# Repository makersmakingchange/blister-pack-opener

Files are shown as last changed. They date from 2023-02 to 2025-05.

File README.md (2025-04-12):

# Blister Pack Opener
The Blister Pack Opener is designed to help users with arthritis or limited hand strength open blister packs of pills.

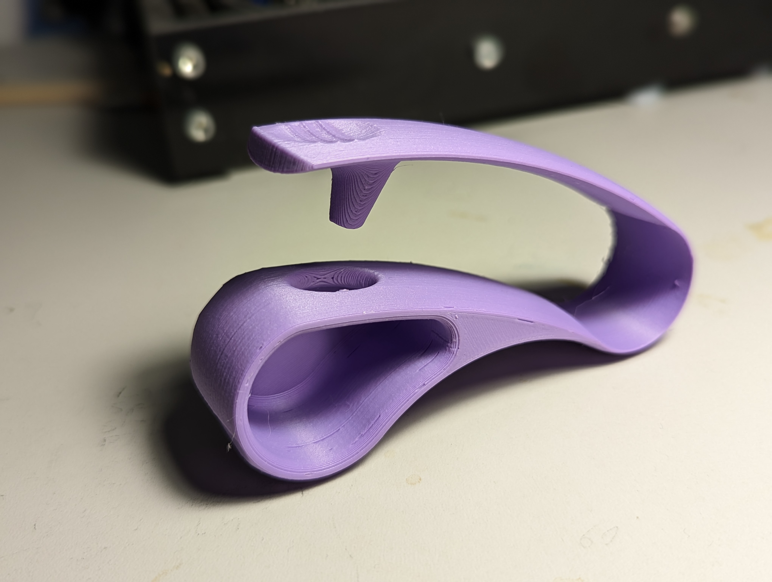
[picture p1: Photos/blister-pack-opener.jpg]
Picture of Blister Pack Opener.


## More info at
- [Makers Making Change Project Page](https://www.makersmakingchange.com/s/product/blister-pack-opener/01tJR0000009H85YAE)

## How to Obtain a Blister Pack Opener
### 1. Do it Yourself (DIY) or Do it Together (DIT)

This is an open-source assistive technology, so anyone is free to build it. All of the files and instructions required to build the Blister Pack Opener are contained within this repository. Refer to the Maker Checklist below.

### 2. Request a build of this device

If you would like to obtain a Blister Pack Opener, you may submit a build request through the [MMC Library Page](https://www.makersmakingchange.com/s/product/blister-pack-opener/01tJR0000009H85YAE). The requestor is responsible for the cost of materials and any shipping.

### 3. How to build this device for someone else

If you have the skills and equipment to build this device, and would like to donate your time to create the switch for someone who needs it, visit the [MMC Maker Wanted](https://makersmakingchange.com/maker-wanted/) section.

## Getting Started

### 1. Read the Makers Checklist

[The Makers Checklist](/Documentation/Blister_Pack_Opener_Maker_Checklist_V1.0.pdf)

### 2. Order the Off-The-Shelf Components

The [Bill of Materials](/Documentation/Blister_Pack_Opener_BOM_V1.0.xlsx) lists all of the parts and components required to build the Blister Pack Opener. 

### 3. Print the 3D Printable components

All of the files and individual print files can be in the [/Build_Files/3D_Printing_Files](/Build_Files/3D_Printing_Files/) folder.

## Files
### Documentation
| Document             | Version | Link |
|----------------------|---------|------|
| Design Rationale     | 1.0     | [Blister_Pack_Opener_Design_Rationale](/Documentation/Blister_Pack_Opener_Design_Rationale_V1.0.pdf)     |
| Maker Checklist      | 1.0     | [Blister_Pack_Opener_Maker_Checklist](/Documentation/Blister_Pack_Opener_Maker_Checklist_V1.0.pdf)     |
| Bill of Materials    | 1.0     | [Blister_Pack_Opener_Bill_of_Materials](/Documentation/Blister_Pack_Opener_BOM_V1.0.xlsx)     |
| 3D Printing Guide    | 1.0     | [Blister_Pack_Opener_3D_Printing_Guide](/Documentation/Blister_Pack_Opener_3D_Printing_Guide_V1.0.pdf)     |
| Assembly Guide       | 1.0     | [Blister_Pack_Opener_Assembly_Guide](/Documentation/Blister_Pack_Opener_Assembly_Guide_V1.0.pdf)     |
| User Guide           | 1.0     | [Blister_Pack_Opener_User_Guide](/Documentation/Blister_Pack_Opener_User_Guide_V1.0.pdf)    |
| Changelog            | 1.0     | [Blister_Pack_Opener_Changelog](/Documentation/Blister_Pack_Opener_Changelog_V1.0.pdf)     |

### Design Files
 - [CAD Files](/Design_Files/CAD_Files)

### Build Files
 - [3D Printing Files](/Build_Files/3D_Printing_Files)

## Attribution

Designers:
 - Design and documentation by Neil Squire Society/Makers Making Change

## License
Everything needed or used to design, make, test, or prepare the Blister Pack Opener is licensed under the [Attribution-NonCommercial-ShareAlike 4.0 ](https://creativecommons.org/licenses/by-nc-sa/4.0/).

Accompanying material such as instruction manuals, videos, and other copyrightable works that are useful but not necessary to design, make, test, or prepare the Blister Pack Opener are published under a Creative Commons Attribution-ShareAlike 4.0 license https://creativecommons.org/licenses/by-sa/4.0/ (CC BY-SA 4.0).

---

<!-- ABOUT MMC START -->
## About Makers Making Change
[Makers Making Change Logo](https://www.makersmakingchange.com/)

Makers Making Change is a program of [Neil Squire](https://www.neilsquire.ca/), a Canadian non-profit that uses technology, knowledge, and passion to empower people with disabilities.

Makers Making Change leverages the capacity of community based Makers, Disability Professionals and Volunteers to develop and deliver affordable Open Source Assistive Technologies.

 - Website: [www.MakersMakingChange.com](https://www.makersmakingchange.com/)
 - GitHub: [makersmakingchange](https://github.com/makersmakingchange)
 - Bluesky: [@makersmakingchange.bsky.social](https://bsky.app/profile/makersmakingchange.bsky.social)
 - Instagram: [@makersmakingchange](https://www.instagram.com/makersmakingchange)
 - Facebook: [makersmakechange](https://www.facebook.com/makersmakechange)
 - LinkedIn: [Neil Squire Society](https://www.linkedin.com/company/neil-squire-society/)
 - Thingiverse: [makersmakingchange](https://www.thingiverse.com/makersmakingchange/about)
 - Printables: [MakersMakingChange](https://www.printables.com/@MakersMakingChange)

### Contact Us
For technical questions, to get involved, or to share your experience we encourage you to [visit our website](https://www.makersmakingchange.com/) or [contact us](https://www.makersmakingchange.com/s/contact).
<!-- ABOUT MMC END -->

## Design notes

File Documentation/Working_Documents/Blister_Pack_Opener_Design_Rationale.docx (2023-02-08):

# Introduction

The Blister Pack Opener is designed to help users with arthritis or limited hand strength open blister packs of pills.

# Research

Name | Picture | Price | Link

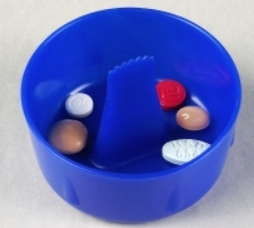
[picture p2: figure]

Blister Pack Opener | | Not Available | Link (https://at-aust.org/items/6725)

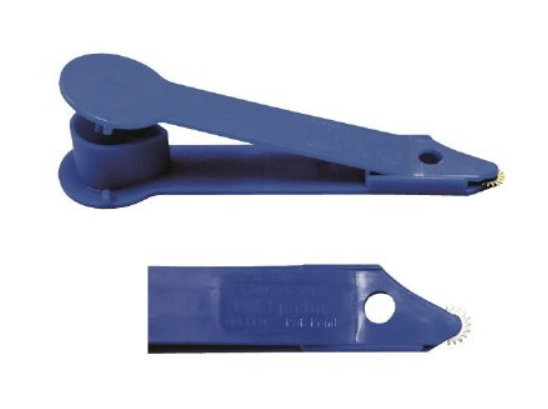
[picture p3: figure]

Pill Ejector | | $7.79 | Link (https://www.ocelco.com/store/pc/Pill-Ejectors-c1835.htm)

# Requirements

## Goals

G01 | The device must open blister packs with minimal force

## Functional Requirements

F01 | The device must be operated with one hand
F02 | The device should allow for opening blister packs using the whole hand
F03 | The device should allow for opening blister packs with minimal force

## Non-functional Requirement

NF01 | The device must be printable with no supports

## Constraints

C01 | Must be entirely 3D printed

# Testing

The device was tested on various blister packs, it worked well on smaller pills, but was too small to accommodate Day-Quil blister packs.

# Opportunities for Improvement

The hole could be made larger to accommodate for larger pills.

© 2023 by Neil Squire. This work is licensed under the CC BY SA 4.0 License: http://creativecommons.org/licenses/by-sa/4.0 Files available at https://makersmakingchange.com/project/blister-pack-opener/ Page 1 of 1

V1.0 | February 2023 Blister Pack Opener Design Rationale

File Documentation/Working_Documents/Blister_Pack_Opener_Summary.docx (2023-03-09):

# Title

Blister Pack Opener

## Subtitle

The Blister Pack Opener is designed to help users with arthritis or limited hand strength open blister packs of pills.

## Device Details

### Overview

The Blister Pack Opener is designed to help users with arthritis or limited hand strength open blister packs of pills.

### Usage

To use, place the blister pack so the flat side is over the hole, and the pill is facing the pin. Squeeze the handle so that the pill is popped out of the blister pack so that the pill pops out into the pocket in the handle.

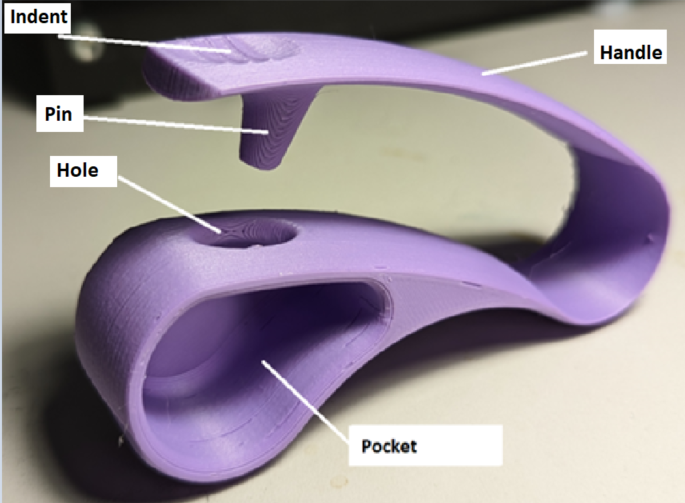
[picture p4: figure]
Blister Pack opener with all features labeled

### Cost

<$1

#### Skills Required

- 3D Printing

#### Time Required

- 3D printing time: 2h58min

#### Tools

- 3D Printer

### Attribution

- Design and documentation by Neil Squire Society/Makers Making Change

© 2023 by Neil Squire. This work is licensed under the CC BY SA 4.0 License: http://creativecommons.org/licenses/by-sa/4.0 Files available at https://makersmakingchange.com/project/blister-pack-opener/ Page 1 of 1

V1.0 | February 2023 Blister Pack Opener Summary

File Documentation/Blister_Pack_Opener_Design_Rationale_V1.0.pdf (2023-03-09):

V1.0 | February 2023

## Blister Pack Opener

## DESIGN RATIONALE

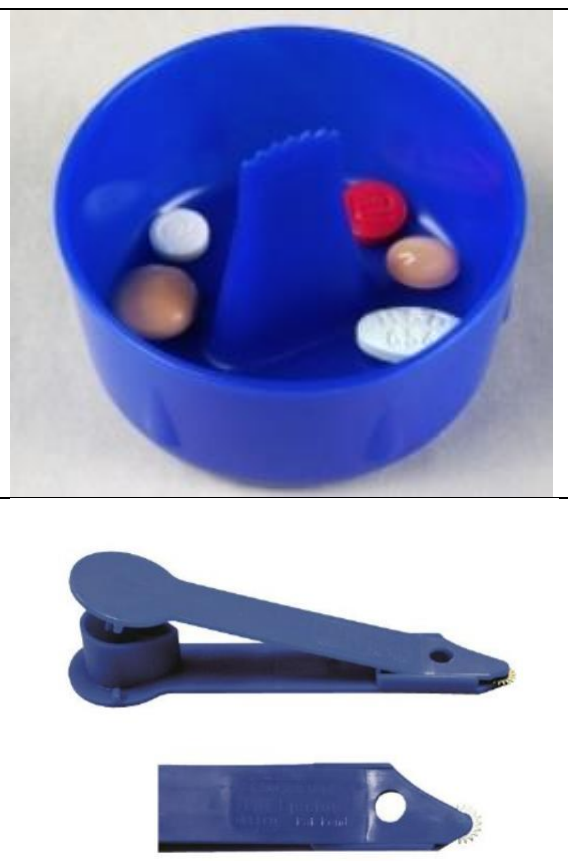
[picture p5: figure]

© 2023 by Neil Squire. (https://neilsquire.ca/)
This work is licensed under the CC BY SA 4.0 License: http://creativecommons.org/licenses/by-sa/4.0
Files available at https://makersmakingchange.com/project/blister-pack-opener/ | Page 1 of 15

### Introduction

The Blister Pack Opener is intended to make it easier to remove medication (e.g., pills) from blister packs. This may be useful for people with limited hand strength or dexterity, such as those with arthritis.

### Research

### Commercial Options

Existing commercial solutions were found by doing a web search for ‘Pill Opener’ and ‘Blister Pack Opener’.

Name | Picture | Price | Link
Blister Pack Opener | | Not Available | Link (https://at-aust.org/items/6725)
Pill Ejector | | $7.79 | Link (https://www.ocelco.com/store/pc/Pill-Ejectors-c1835.htm)

## DESIGN RATIONALE

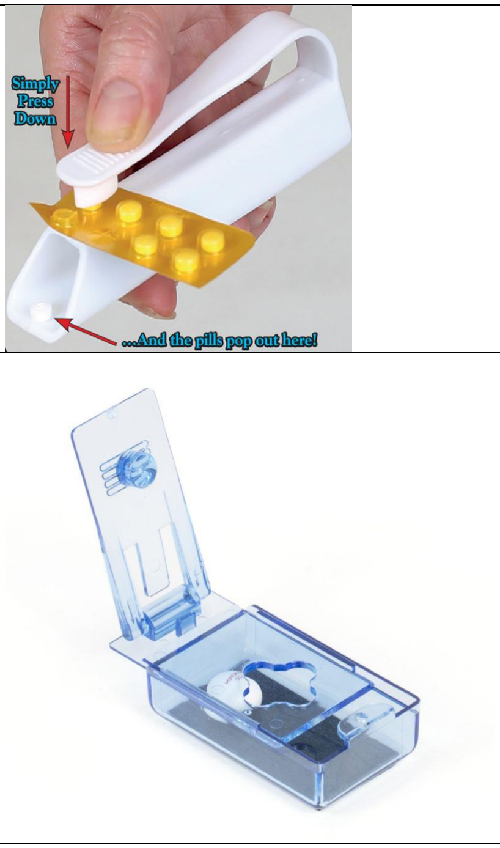
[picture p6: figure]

Files available at https://makersmakingchange.com/project/blister-pack-opener/ | Page 2 of 15

Easy
Open
Pill
Popper
Tool
$8.90 | Link (https://www.healthpride.com.au/product/Easy-Open-Pill-Popper-Tool/1876)

Tablet
Puncher
– Blister
Opener
n/a | n/a

## DESIGN RATIONALE

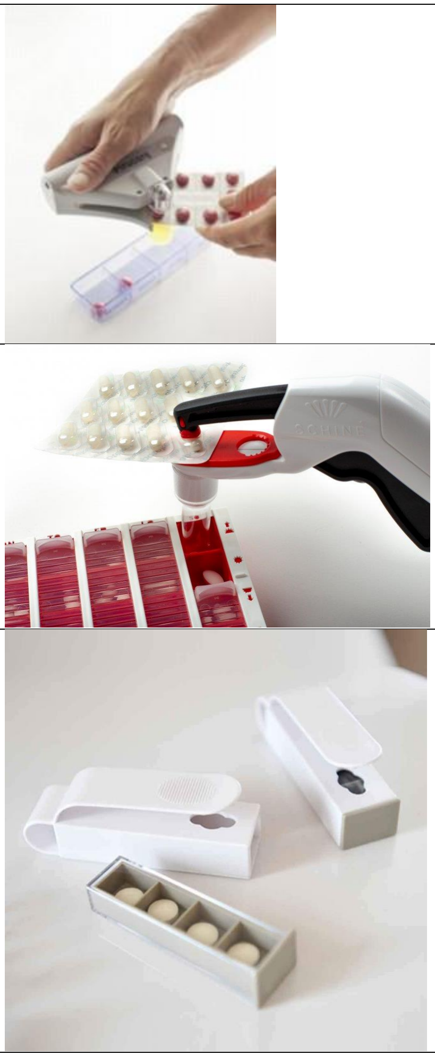
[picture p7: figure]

Files available at https://makersmakingchange.com/project/blister-pack-opener/ | Page 3 of 15
Pirucare – blister pack opener | Discontinued since 31-10-2016 | Link (https://hmi-basen.dk/en/r11x.asp?linkinfo=36111)
Pill Handle | | Link (https://www.livetsomsenior.dk/pillehandtag)
$32 | Amazon Purchase Page (https://www.amazon.ca/Celiy-Arthritis-Dispenser-Housekeeping-Organizers/dp/B089652RNK)

## DESIGN RATIONALE

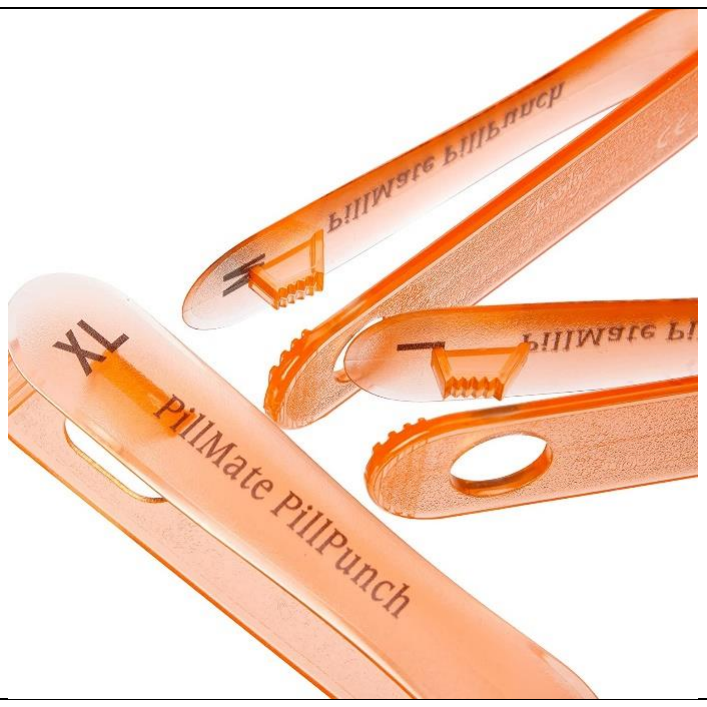
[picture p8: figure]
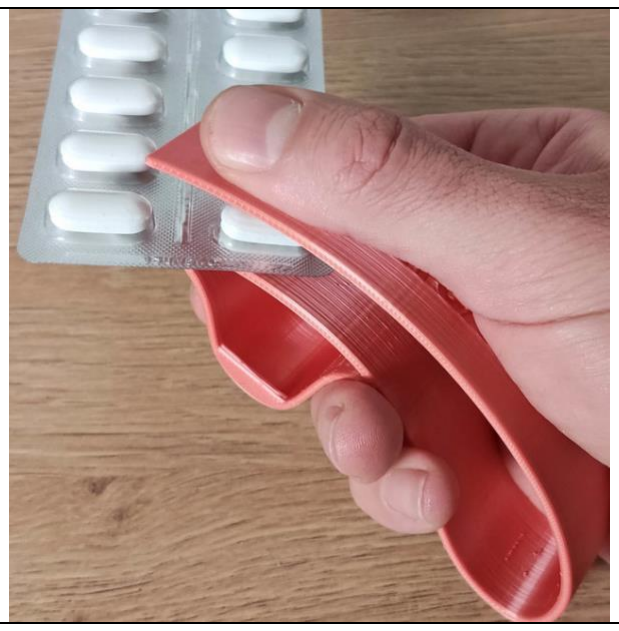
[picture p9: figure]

Files available at https://makersmakingchange.com/project/blister-pack-opener/ | Page 4 of 15

Pillmate
Pill
Punch

$13, low
stock

Pillmate
Pill
Punch -
Amazon (https://www.amazon.ca/Shantys-PillMate-PillPunch-Random-Colour/dp/B001KUA220)

### Existing DIY Options

Name | Picture | Price | Link
Pill Puncher | | N/A | Link (https://cults3d.com/en/3d-model/tool/pillikan-easy-to-print-pill-puncher)

## DESIGN RATIONALE

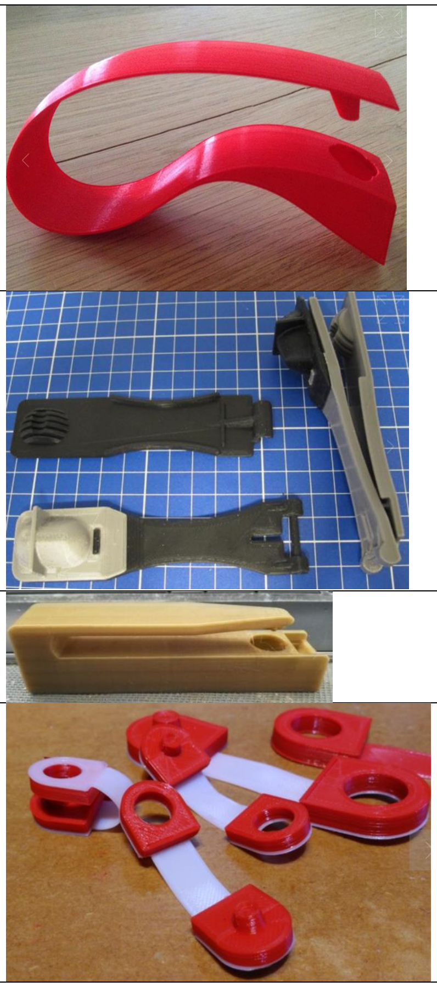
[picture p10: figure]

Files available at https://makersmakingchange.com/project/blister-pack-opener/ | Page 5 of 15
Pill Puncher | N/A | Link (https://www.thingiverse.com/thing:1630353)
Blister Pack Opener | N/A | Link (https://www.thingiverse.com/thing:3080416)
Blister Tablet Opener | N/A | Link (https://www.thingiverse.com/thing:2846756)
| | Link (https://www.thingiverse.com/thing:2711263)

## DESIGN RATIONALE

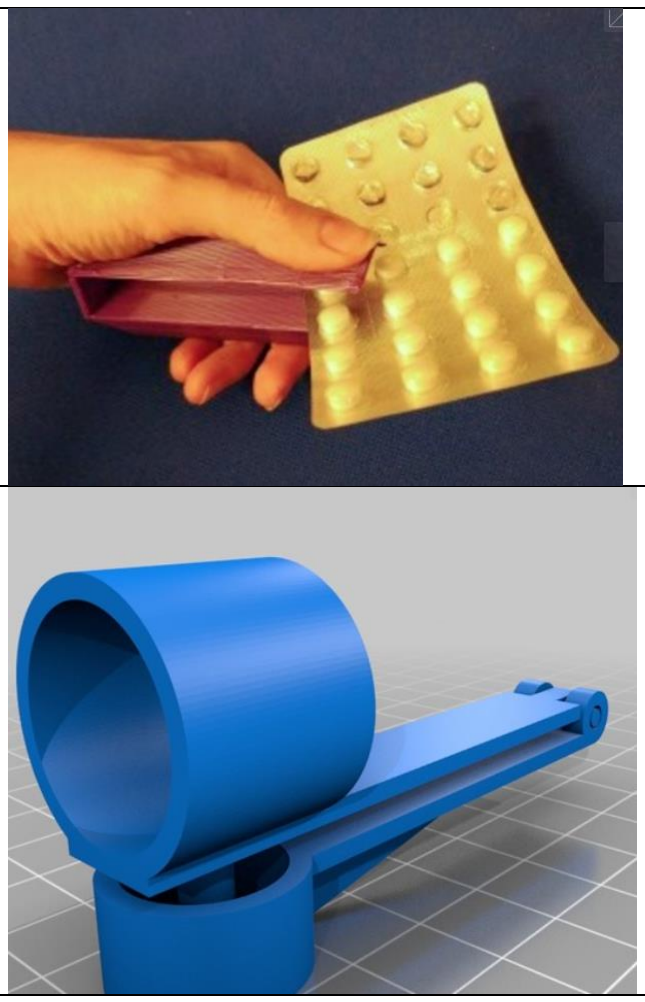
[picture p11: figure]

Files available at https://makersmakingchange.com/project/blister-pack-opener/ | Page 6 of 15

Link (https://www.thingiverse.com/thing:2926687)

Link (https://www.thingiverse.com/thing:2425976)

## DESIGN RATIONALE

Files available at https://makersmakingchange.com/project/blister-pack-opener/ | Page 7 of 15

### Requirements

### Goals

G01 | The device must make it easier to remove items from blister packs by reducing the required dexterity or required force or both.
G02 | The device should work with a range of pill shapes and sizes.
G03 | The device should make it less likely to lose the pill.

### Functional Requirements

F01 | The device must be operable with one hand.
F02 | The device should allow for opening blister packs using force generated by the whole hand.
F03 | The device should allow for opening blister packs with minimal force
F04 | The device must have a means from preventing the pill from getting lost.
F05 | The device must provide enable the user to easily retrieve the pill after its removed from the blister pack.
F06 | (Range of pill sizes)
F07 | (Number of cycles to failure)

### Non-functional Requirement

NF01 The device should be printable with no supports

### Constraints

C01 Should be entirely 3D printed

### Existing Devices

### Pill Release for Blister Packs

https://www.thingiverse.com/thing:5572151

## DESIGN RATIONALE

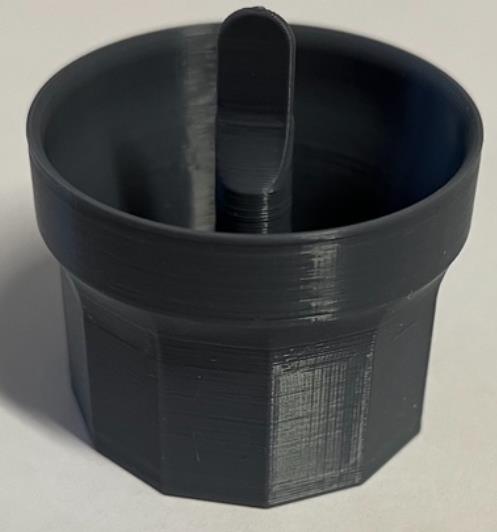
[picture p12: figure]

Files available at https://makersmakingchange.com/project/blister-pack-opener/ | Page 8 of 15

Author: Elppa8

License: Creative Commons - Attribution

Cost: 12g of filament

Print Time: 1h40min

Summary
A cup with a large fin coming out of the centre. The fin can be used to remove the pill from the pack, which then falls into the cup.

Print Testing
Device printed easily with no supports

Functional Testing
Unintuitive on how to use. Broke when opening a gum blister pack.

Opportunities for Improvements
Fin can be improved to withstand more torque.

## DESIGN RATIONALE

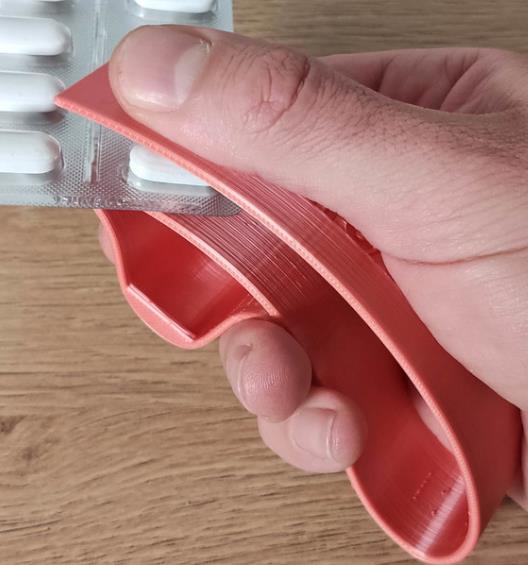
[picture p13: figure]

Files available at https://makersmakingchange.com/project/blister-pack-opener/ | Page 9 of 15

### PILLIKAN - EASY TO PRINT PILL PUNCHER

This design is comprised of a single 3D printed piece. It utilizes a flexure hinge. The pill is pushed into a compartment oriented towards the side of the device.

Author: Brignetti Longoni

License: Creative Commons Attribution

Cost: 20g filament

Print Time: 3h22min

Print Testing
The print was tested on its side with no supports and printed with no issues

Functional Testing
Device was used to open a Day-Quil Pack and a gum package, as those were the only blister packs on hand. It was found that both packages were too large to fit through the hole on the print.

Closing force: ~150 gf

Opportunities for Improvements
- Handle could be made stiffer to transfer force better without bending
- The handle could have a slight curve to make it fit the hand better
- Sharp edges can be made smoother
- Mouse ears can be added to prevent the print from peeling

## DESIGN RATIONALE

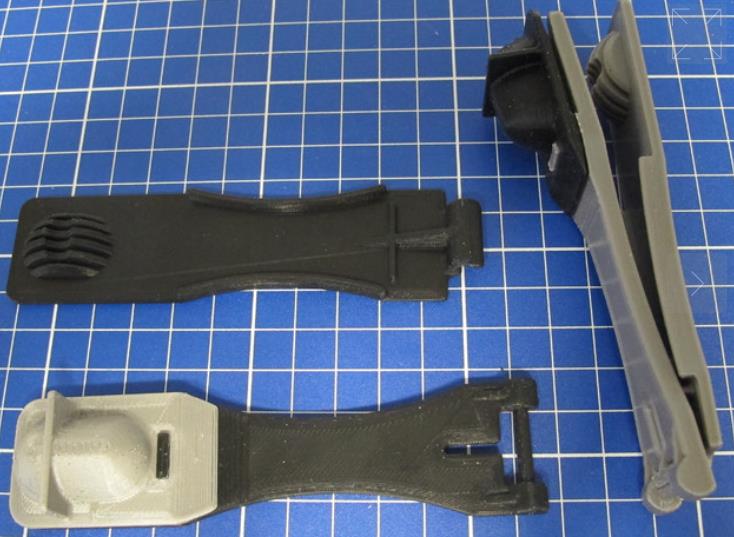
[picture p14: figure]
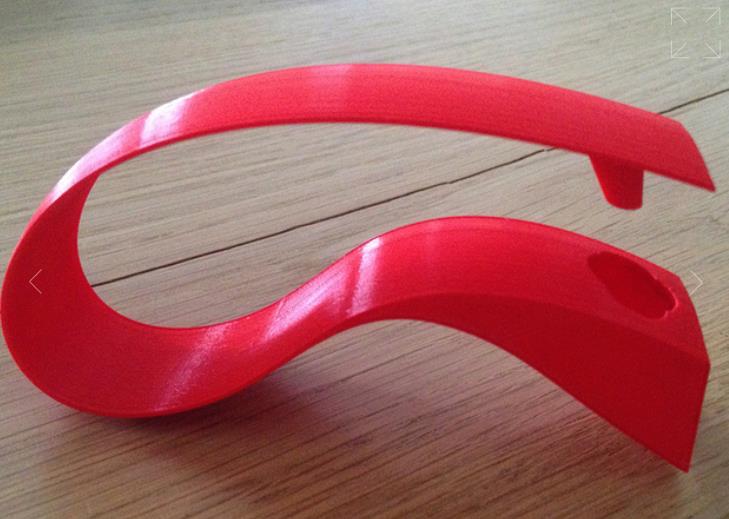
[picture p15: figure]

Files available at https://makersmakingchange.com/project/blister-pack-opener/ | Page 10 of 15

### Blister pack opener

(Summary)

Author: Joep Welling

License: Creative Commons - Attribution - Share Alike

Cost: 32g of filament

Print Time: 4h32min

### Pill Puncher

Author: Ivery Barel

License: CC-BY-NC-ND

Cost: 21 g of filament

Print Time: 3h11min

## DESIGN RATIONALE

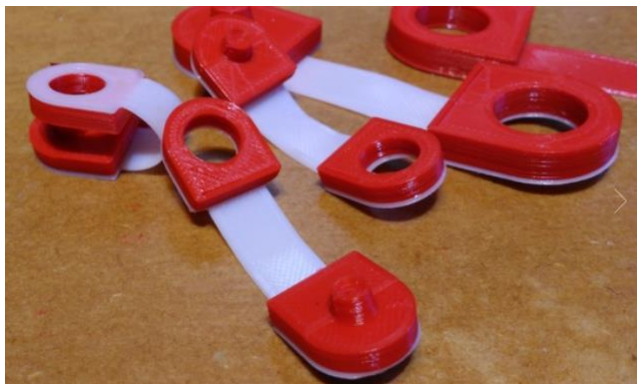
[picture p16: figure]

Files available at https://makersmakingchange.com/project/blister-pack-opener/ | Page 11 of 15

Summary
This design is comprised of a single 3D printed piece. It utilizes a flexure hinge. The pill is pushed into a compartment oriented towards the front of the device.

Print Testing
The print was tested on its side with no supports and printed with no issues

Functional Testing
This design also tend to cause the pills to fly out of the pocket and out the end of the device. Some users have reported that this design tends to crack where the pills come out.

Closing force: ~200 gf

Opportunities for Improvements
- The design has sharp corners along the handle and on the ends of the handle.
- The pill compartment section could have additional material added to resist the force applied by the ejector and reduce the likelihood of cracking
- The handle portion may not be stiff enough, so that the device doesn’t work well unless the user applies force directly over the ejector pin. A rib or additional material could be added to stiffen this section.
- Add a mouse ear to the end of the handle so the print is less likely to warp

Conclusion

### Blister Pack Pill Popper

https://www.thingiverse.com/thing:2711263

## DESIGN RATIONALE

Files available at https://makersmakingchange.com/project/blister-pack-opener/ | Page 12 of 15

Author: M Craig

License: Creative Commons - Attribution - Non-Commercial

Cost: 2g of filament

Print Time: 15min

Summary
Design consists of two roughly half circle shaped tabs connected by a thin piece of plastic. One tab has a horn to push out the pill, and the other tab has a hole to allow the pill to be removed. The design allows the user to apply force over a larger area.

Print Testing
Design printed quickly with no supports

Functional Testing
No pills small enough to test with. The thin connecting piece of plastic had to be bent while still hot and quickly developed fatigue lines.

Opportunities for Improvements
A more flexible filament could be used for the connector

### Comparison

### Pill Opener

https://www.thingiverse.com/thing:5780009

## DESIGN RATIONALE

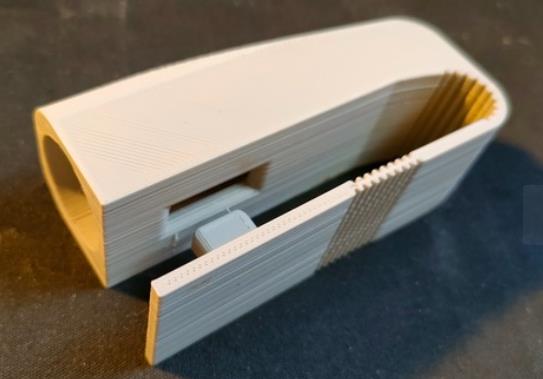
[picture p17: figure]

Files available at https://makersmakingchange.com/project/blister-pack-opener/ | Page 13 of 15

Author: Daniel Walsh

License: Creative Commons - Attribution - Non-Commercial - Share Alike

Cost: 36 g of filament

Print Time: 5:46

### Testing

The device was tested on various blister packs, it worked well on smaller pills, but was too small to accommodate Day-Quil blister packs.

### Opportunities for Improvement

The hole could be made larger to accommodate for larger pills.

Add tactile indication of where user should put thumb

## DESIGN RATIONALE

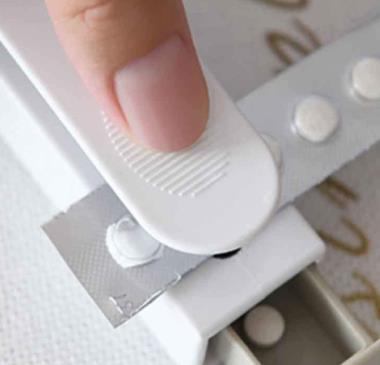
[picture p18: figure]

Files available at https://makersmakingchange.com/project/blister-pack-opener/ | Page 14 of 15

### Design

### Design 0.1

Summary
This design is similar to the Pill Puncher by Ivery Barel. The pill pocket opens towards the front.

Functional Testing
The design felt comfortable in the hand. The handle is significantly stiffer and requires greater force to close.

The puncher successfully removed the pill from the package, but it hit the bottom surface of the pill pocket and ricocheted out of the device.

Closing force: ~1500 gf

Opportunities for Improvements
1. Reduce the stiffness of the handle.
2. Move to a side pocket design to better contain the pill after its removed from the package.
3. Add concave depression to the thumb guide.
4. Reduce sharp edges and corners

### Design 0.2

Summary
This design incorporates some of the OFIs from Design 0.1:
- Concave thumb groove
- Rounded corners
- Side Pocket

## DESIGN RATIONALE

Files available at https://makersmakingchange.com/project/blister-pack-opener/ | Page 15 of 15

Print Testing
Cost: 22g of filament

Print Time: 3:07

Functional Testing
Closing force: ~1100 gf

Device feels comfortable in the hand, but the bulb where the pocket is located takes a while to find the right place to grip it. Notches could be added to find the grip location easier.

Opportunities for Improvements
1. Reduce stiffness
2. Add groove or notch for index finger

### Design 0.3

Summary
This design incorporates some of the OFIs from Design 0.2:
- Reduce stiffness
- Add groove or notch for index finger

Print Testing
Cost: 20g of filament

Print Time: 2:58

Functional Testing
Closing force: ~300 gf

Design is comfortable to hold and much easier to press.

Opportunities for Improvements
1) Improve surfacing of model

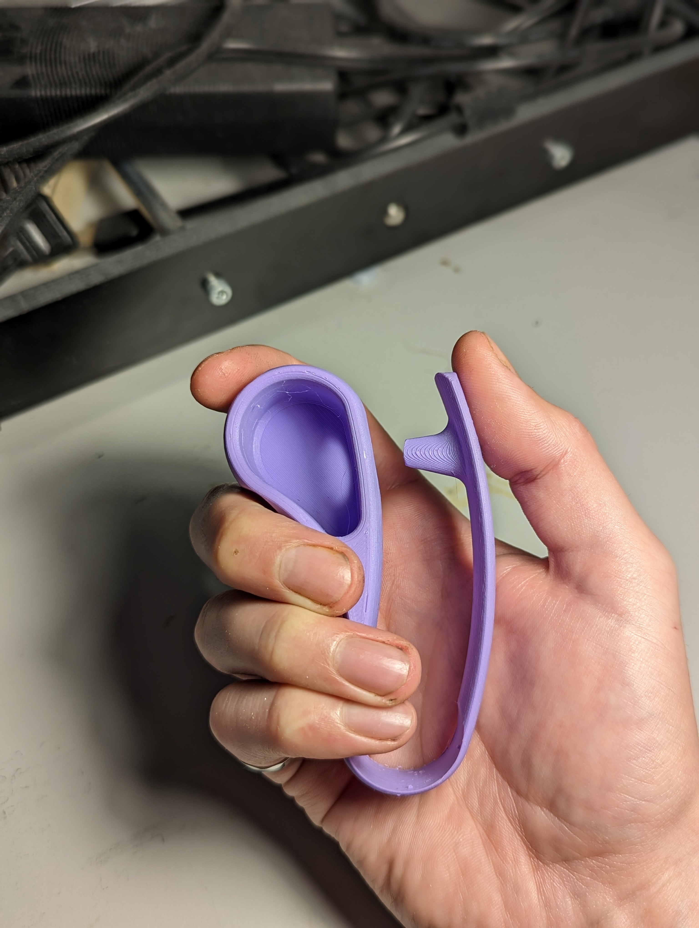
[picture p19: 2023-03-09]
Photos/Feature picture.jpg

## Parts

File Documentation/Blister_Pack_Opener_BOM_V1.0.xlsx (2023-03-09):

Device: Blister Pack Opener |  | Total Cost | Total Print time (hr) | Total filament (g)
Version: V1.0 | Date Created: 2/7/2023 | $0.50 | 0.00 | 20
Commercial Parts:
Part type (Electrical. Mechanical, Sanitization, ect) | Part Name | Quantity Needed | Pkg Quantity | Price per package | Price per Unit | Price for qty needed | Link
 |  |  |  |  |  | $0.00
 |  |  |  |  |  | $0.00
 |  |  |  |  |  | $0.00
3D Printed Parts ESTIMATED PRICING USING 1KG ROLL COST: | $25.00
Part | Description | Quantity Needed | TOTAL Mass (g) | Estimated Price | Print Time (Min) | Link
Pill_Puncher | Main file | 1 | 20 | $0.50
 |  |  |  | $0.00
 |  |  |  | $0.00
 |  |  |  | $0.00
 |  |  |  | $0.00
 |  |  | Total Print Cost: | $0.50
Tools for Assembly
Alternatives (if there are other sources for some parts link them below)
Part and description | Link

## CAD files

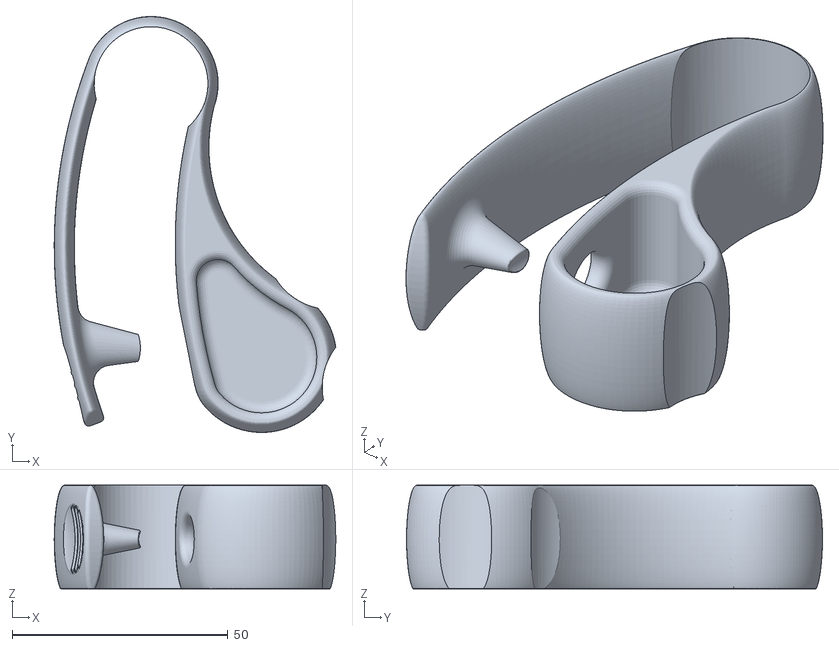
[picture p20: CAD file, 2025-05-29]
Build_Files/3D_Printing_Files/Blister_Pack_Opener.stl
65.3 x 96.4 x 24.0

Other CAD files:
Design_Files/CAD_Files/Blister Pack Opener.step
Design_Files/CAD_Files/Blister Pack Opener.f3d

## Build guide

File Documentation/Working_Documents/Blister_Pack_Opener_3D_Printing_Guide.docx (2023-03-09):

# 3D Printing Summary

Metrics
Total Print Time (min) | 178
Total Number of Components | 1
Typical Total Mass (g) | 20
Typical Number of Print Setups | 1

# 3D Printing Settings

Print File Name | Qty | Total Print Time (hr:min) | Mass (g) | Infill (%) | Support(Y/N) | Layer Height/ Nozzle Diameter(mm) | Notes (orientation, special settings, etc.)
Blister_Pack_Opener.stl | 1 | 2:58 | 20 | 20 | N | 0.2/0.4 | - Print in orientation given in STL - Print with a brim

# Customization Options

- The device can be printed in any colour the user would like.

# Post-Processing

- Remove any sharp edges with sandpaper or a hobby knife

# Examples of Quality Prints

Photos of Blister_Pack_Opener.stl

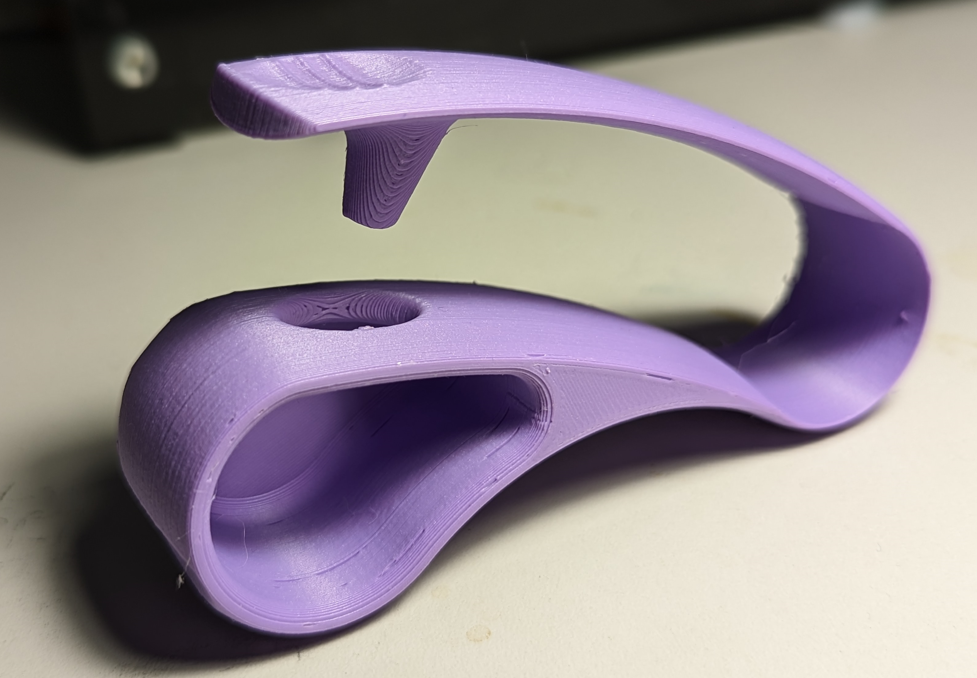
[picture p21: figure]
Blister pack opener example print

© 2023 by Neil Squire. This work is licensed under the CC BY SA 4.0 License: http://creativecommons.org/licenses/by-sa/4.0 Files available at https://makersmakingchange.com/project/blister-pack-opener/ Page 1 of 2

V1.0 | February 2023 Blister Pack Opener 3D Printing Guide

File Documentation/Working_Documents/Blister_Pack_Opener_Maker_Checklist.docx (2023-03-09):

# Maker To Do List

- Read through the Assembly Guide to become familiar with required components, tools, supplies, and safety gear and overall assembly steps.
- Talk to User about customization options (e.g., color, any special requests, etc.)
- Order hardware components
- Gather tools, supplies, and safety equipment.
- Assemble the device
- Test device
- Print “User Quick Guide”

# Items to Give to User

- Assembled, tested device
- “User Quick Guide”

© 2023 by Neil Squire. This work is licensed under the CC BY SA 4.0 License: http://creativecommons.org/licenses/by-sa/4.0 Files available at https://makersmakingchange.com/project/blister-pack-opener/ Page 1 of 1

V1.0 | February 2023 Blister Pack Opener Maker Checklist

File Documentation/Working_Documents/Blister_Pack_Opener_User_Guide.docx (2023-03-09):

## Introduction

The Blister Pack Opener is designed to help users with arthritis or limited hand strength open blister packs of pills.

## Features

Blister Pack Opener with all features labeled

## Usage

To use, place the blister pack so the flat side is over the hole, and the pill is facing the pin. Squeeze the handle so that the pill is popped out of the blister pack so that the pill pops out into the tube in the handle.

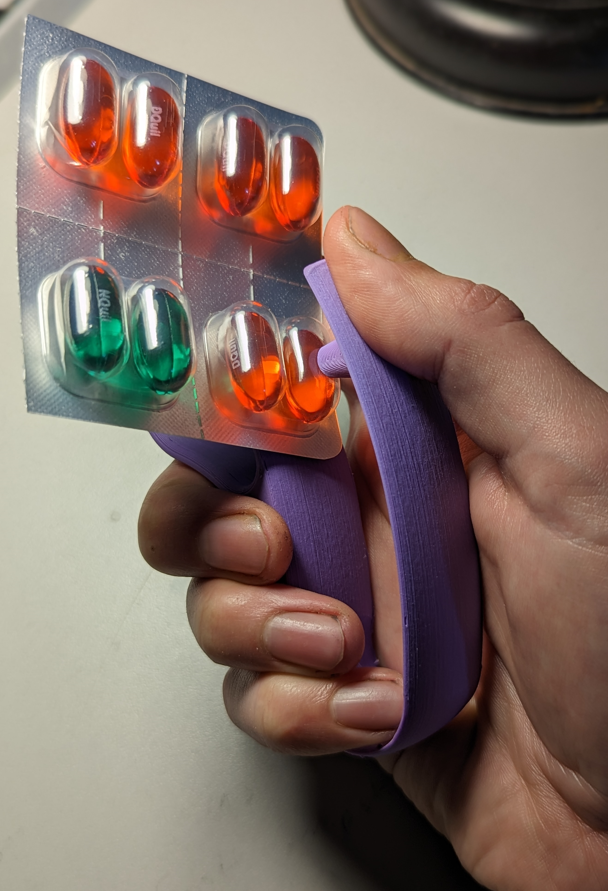
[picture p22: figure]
Blister pack opener in use

## Compatibility

The device works with any pill that fits in a 20x15mm oval.

## Specifications

Length: 10cm

Width: 6cm

Height: 2.5cm

Weight: 20g

## Cleaning

The device can be wiped clean with a damp cloth.

© 2023 by Neil Squire. This work is licensed under the CC BY SA 4.0 License: http://creativecommons.org/licenses/by-sa/4.0 Files available at https://makersmakingchange.com/project/blister-pack-opener/ Page 2 of 3

V1.0 | February 2023 Blister Pack Opener user Quick Guide

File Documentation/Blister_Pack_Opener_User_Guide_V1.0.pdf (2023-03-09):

V1.0 | February 2023

## Blister Pack Opener

## USER QUICK GUIDE

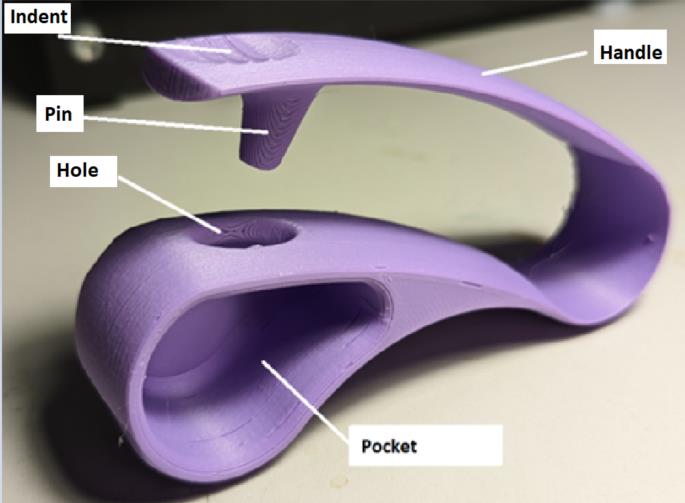
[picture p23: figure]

© 2023 by Neil Squire. (https://neilsquire.ca/)
This work is licensed under the CC BY SA 4.0 License: http://creativecommons.org/licenses/by-sa/4.0
Files available at https://makersmakingchange.com/project/blister-pack-opener/ | Page 1 of 2

### Introduction

The Blister Pack Opener is designed to help users with arthritis or limited hand strength open blister packs of pills.

### Features

### Usage

To use, place the blister pack so the flat side is over the hole, and the pill is facing the pin. Squeeze the handle so that the pill is popped out of the blister pack so that the pill pops out into the tube in the handle.

V1.0 | February 2023

## Blister Pack Opener

## USER QUICK GUIDE

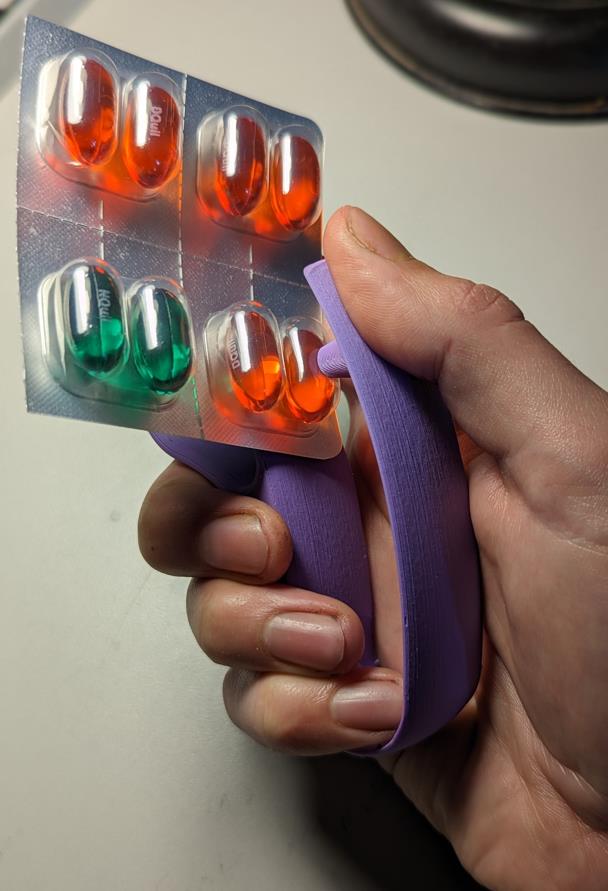
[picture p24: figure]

© 2023 by Neil Squire. (https://neilsquire.ca/)
This work is licensed under the CC BY SA 4.0 License: http://creativecommons.org/licenses/by-sa/4.0
Files available at https://makersmakingchange.com/project/blister-pack-opener/ | Page 2 of 2

### Compatibility

The device works with any pill that fits in a 20x15mm oval.

### Specifications

Length: 10cm

Width: 6cm

Height: 2.5cm

Weight: 20g

### Cleaning

The device can be wiped clean with a damp cloth.

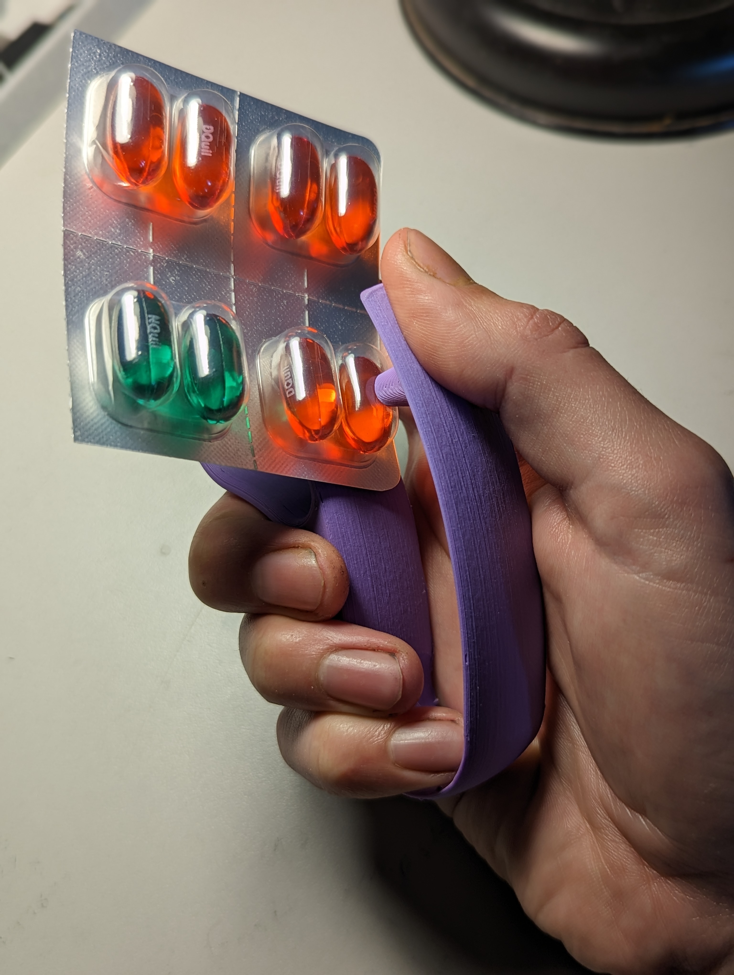
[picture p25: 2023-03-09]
Photos/Usage Picture.jpg

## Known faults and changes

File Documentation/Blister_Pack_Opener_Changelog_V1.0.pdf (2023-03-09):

V1.0 | February 2023

# Blister Pack Opener

# CHANGELOG

© 2023 by Neil Squire. (https://neilsquire.ca/)
This work is licensed under the CC BY SA 4.0 License: http://creativecommons.org/licenses/by-sa/4.0
Files available at https://makersmakingchange.com/project/blister-pack-opener/ | Page 1 of 1

# Version 1.0 | 2023/03/06

## - Design and documentation by Neil Squire Society/Makers Making Change

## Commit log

2023-02-08 Moved everything up a folder
    [Blister_Pack_Opener_BOM.xlsx, Pill_Puncher.stl]
2023-02-08 Fixed links
    Removed link to cad in readme, renamed BOM
    [Blister_Pack_Opener_BOM_V1.0.xlsx]
2023-03-09 Update with new CAD file
    [Blister Pack Opener.f3d, Blister_Pack_Opener.stl, Blister_Pack_Opener_BOM.xlsx, Blister_Pack_Opener_BOM_V1.0.xlsx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]
2025-05-29 Printability improvements
    Increased the print surface to increase printability
    [Blister Pack Opener.f3d, Blister_Pack_Opener.stl]
2025-05-29 changed default orientation
    [Blister_Pack_Opener.stl]
2025-05-29 Create Blister Pack Opener.step
    Added step file for device
    [Blister Pack Opener.step]
